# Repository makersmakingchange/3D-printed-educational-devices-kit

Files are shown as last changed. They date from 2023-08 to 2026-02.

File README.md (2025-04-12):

# 3D-Printed-Educational-Devices-Kit
<!--- 
SUMMARY
 --->

The [3D Printed Educational Devices Kit](https://www.makersmakingchange.com/s/product/3d-printed-educational-devices-kit/01tJR0000006949YAA) contains devices that support people with disabilities in activities of daily living and learning. These devices assist people with arthritis, limited finger exterity or other disabilities. This kit gives schools a great introduction into the world of 3D printed Assistive Technology (AT).

## 3D Printed Educational Devices Kit
### Summary

| Name                 | Repository Link |
|----------------------|-----------------|
| Bottle Opener        | https://makersmakingchange.com/s/product/bottle-opener/01tJR00000068z0YAA |  
| Key Turner           |  https://www.makersmakingchange.com/s/product/key-turner/01tJR00000068z6YAA  |
| Pen Ball             | https://www.makersmakingchange.com/s/product/pen-ball/01tJR00000068zzYAA |
| Palm Pen Holder      | https://www.makersmakingchange.com/s/product/palm-pen-holder/01tJR00000068z8YAA |
| Ready Bar Flat       | https://makersmakingchange.com/s/product/reading-bar-flat/01tJR00000068z3YAA |
| Dice Spinner         | https://makersmakingchange.com/s/product/dice-spinner/01tJR000000693qYAA |
| MMC60 Switch         | https://makersmakingchange.com/s/product/mmc60-switch/01tJR000000693rYAA |

### Bottle Opener
This device provides a large gripping surface and clamps onto the caps of standard water bottles with a small squeeze, allowing users to remove or screw on water bottle caps.

### Key Turner
Users loop their finger through the hole and twist to lock and unlock doors with minimal wrist movement. The large key bed can accommodate various shape of key heads.

### Pen Ball
The pen ball makes it easier to grip a pen, pencil, or other writing utensils.

### Palm Pen Holder
Users can gently curl their fingers around a handle to hold it securely or hook their thumb around the writing utensil

### Reading Bar Flat
The dyslexia bar is a tool that isolates text on a page so readers can focus on reading one or two lines at a time. This reading bar can be used on flat documents and sheets of paper.

### Dice Spinner
The switch activated dice spinner utilizes a hobby motor, battery holder, and jack along with a couple 3d printed parts and a clear plastic cup to make any dice game more accessible. It is an easy toy to make that allows children to roll the dice in an alternative way.

### MMC60 Switch
The switch is activated by applying pressure on the top surface. This switch can be connected to any standard AT interface, and can also be used with the Xbox Adaptive Controller. The kit contains different colours and textures of interchangeable button tops.

----

<!-- ABOUT MMC START -->
## About Makers Making Change
[Makers Making Change Logo](https://www.makersmakingchange.com/)

Makers Making Change is a program of [Neil Squire](https://www.neilsquire.ca/), a Canadian non-profit that uses technology, knowledge, and passion to empower people with disabilities.

Makers Making Change leverages the capacity of community based Makers, Disability Professionals and Volunteers to develop and deliver affordable Open Source Assistive Technologies.

 - Website: [www.MakersMakingChange.com](https://www.makersmakingchange.com/)
 - GitHub: [makersmakingchange](https://github.com/makersmakingchange)
 - Bluesky: [@makersmakingchange.bsky.social](https://bsky.app/profile/makersmakingchange.bsky.social)
 - Instagram: [@makersmakingchange](https://www.instagram.com/makersmakingchange)
 - Facebook: [makersmakechange](https://www.facebook.com/makersmakechange)
 - LinkedIn: [Neil Squire Society](https://www.linkedin.com/company/neil-squire-society/)
 - Thingiverse: [makersmakingchange](https://www.thingiverse.com/makersmakingchange/about)
 - Printables: [MakersMakingChange](https://www.printables.com/@MakersMakingChange)

### Contact Us
For technical questions, to get involved, or to share your experience we encourage you to [visit our website](https://www.makersmakingchange.com/) or [contact us](https://www.makersmakingchange.com/s/contact).
<!-- ABOUT MMC END -->

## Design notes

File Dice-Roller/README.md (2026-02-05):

# Rumble Plate Dice Roller
A switch adapted device to roll the dice for any game night!

This switch activated dice roller utilizes a hobby motor, battery holder, Omron switch, and 3.5mm jack along with a couple 3d printed parts and a clear plastic cup to make any dice game more accessible. This device is a new development of the Dice Spinner that features faster dice rolling and variations in allowable cup size.

The Rumble Plate Dice Roller allows for approximately 10oz to 22oz clear plastic cups. Following the assembly guide, the components can be wired and mounted, then the dice roller is all ready to use! It is an easy toy to make that allows people to roll the dice in an alternative way.

## Usage

An AT switch can be plugged into the 3.5mm jack on the side of the device to be used for activation. Alternatively, the on-device switch can be used for activation. The on-device button would be meant more for others playing around the table who are able to reach over and wrap their hands around the base to push the button. With the additional print of the vertical push base, the on-device button can be used to turn the device itself into the activation button such that anyone around the table can push on to top of  the clear cup to roll the dice. This on-device button can be used in tandem with the corded AT switch.

## Required Skills:

 - Soldering
 - 3D Printing

## Required Components

 - Motor
 - AAA Battery Holder
 - Velcro
 - Omron Switch
 - 3.5mm Jack
 - Clear Plastic Cup
 - Dice
 - 3D Printed Parts

## Printing Instructions

- Print the STL files in their given orientations
- 0.3 mm Layer height
- No supports
- No brim

## Build Instructions

This device consists of several 3D printed components and electrical components that assemble together and can be used in tandem with an assistive switch. All STL’s and documentation can be found in the downloadable maker files in the GitHub Repository.

<!-- ABOUT MMC START -->
## About Makers Making Change
[Makers Making Change Logo](https://www.makersmakingchange.com/)

Makers Making Change is a program of [Neil Squire](https://www.neilsquire.ca/), a Canadian non-profit that uses technology, knowledge, and passion to empower people with disabilities.

Makers Making Change leverages the capacity of community based Makers, Disability Professionals and Volunteers to develop and deliver affordable Open Source Assistive Technologies.

 - Website: [www.MakersMakingChange.com](https://www.makersmakingchange.com/)
 - GitHub: [makersmakingchange](https://github.com/makersmakingchange)
 - Bluesky: [@makersmakingchange.bsky.social](https://bsky.app/profile/makersmakingchange.bsky.social)
 - Instagram: [@makersmakingchange](https://www.instagram.com/makersmakingchange)
 - Facebook: [makersmakechange](https://www.facebook.com/makersmakechange)
 - LinkedIn: [Neil Squire Society](https://www.linkedin.com/company/neil-squire-society/)
 - Thingiverse: [makersmakingchange](https://www.thingiverse.com/makersmakingchange/about)
 - Printables: [MakersMakingChange](https://www.printables.com/@MakersMakingChange)

### Contact Us
For technical questions, to get involved, or to share your experience we encourage you to [visit our website](https://www.makersmakingchange.com/) or [contact us](https://www.makersmakingchange.com/s/contact).
<!-- ABOUT MMC END -->

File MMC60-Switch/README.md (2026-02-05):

<!-- Open Source Assistive Technology: GitHub Readme Template Version 1.1 (2024-Mar-15) -->

<!---
INSTRUCTIONS
This is a markdown template for creating the README.md file in a GitHub repository. This file is rendered and displayed automatically when someone visits the repository.

This document includes helper text that will not be displayed when rendered. Any text between the less-than sign + exclamation mark + three hyphen-minus (<!---) and matching three hyphen-minus + greater-than sign will not be displayed. This helper text can be deleted once the corresponding section is completed.

This template has a number of fields that can be searched and replaced with other text:
 - <Device_Name> Replace this with filename-friendly version of the device with underscores. e.g., Open_Wobble_Switch
 - <DeviceName> Replace this with the human-readable name of the device with spaces. e.g., Open Wobble Switch
 - <DesignerName> Replace this with the person or organization responsible for the design. e.g., John Doe.
 - <RepositoryLink> Replace this with the web address for the repository. e.g., (e.g., https://github.com/makersmakingchange/Open-Wobble-Switch))
 - <MMCWebLink> This is an alphanumeric id for the Makers Making Change Website. e.g., 01tJR000000698oYAA. This will come from MMC staff. 
 --->
 
 <!--- 
TITLE
Should match the name of the GitHub repository. Choose something descriptive rather than whimsical. 
 --->
# MMC60 Assistive Switch

2025-May-02: This repository is in the process of updating.

<!--- SUMMARY A brief summary of the project. What it does, who it is for, how much it costs.  --->
The <DeviceName> is an assistive technology widget that makes it easier to document Open-Source Assistive Technology devices. 

It is intended for use by makers. 

The device is comprised of off-the-shelf electronics and 3D printed parts. 

The overall cost of materials is about $<MaterialCost> (plus $<ShippingCost> for component shipping).

Picture of <DeviceName>.

## More info at
- [Makers Making Change Assistive Device Library Listing](<MMCWebLink>)

## How to Obtain the Device
### 1. Do-it-Yourself (DIY) or Do-it-Together (DIT)

This is an open-source assistive technology, so anyone is free to build it. All of the files and instructions required to build the device are contained within this repository. Refer to the Maker Guide below.

### 2. Request a build of this device

You may also submit a build request through the [Makers Making Change Assistive Device Library Listing](<MMCWebLink>) to have a volunteer maker build the device. As the requestor, you are responsible for reimbursing the maker for the cost of materials and any shipping.

### 3. Build this device for someone else

If you have the skills and equipment to build this device, and would like to donate your time to create the device for someone who needs it, visit the [MMC Maker Wanted](https://makersmakingchange.com/maker-wanted/) section.

## Build Instructions

### 1. Read through the Maker Guide

The [Maker Guide](/Documentation/<Device_Name>_Maker_Guide.pdf)  contains all the necessary information to build this device, including tool lists, assembly instructions, programming instructions (if applicable) and testing.

### 2. Order the Off-The-Shelf Components

The [Bill of Materials](/Documentation/<Device_Name>_BOM.xlsx) lists all of the parts and components required to build the device.

### 3. Print the 3D Printable components

All of the files and individual print files can be in the [/Build_Files/3D_Printing_Files](/Build_Files/3D_Printing_Files/) folder.

### 4. Assemble the <DeviceName>

Reference the [Assembly Guide](/Documentation/<Device_Name>_Assembly_Guide.pdf) for the tools and steps required to build each portion.

## How to improve this Device
As open source assistive technology, you are welcomed and encouraged to improve upon the design. 

## Files
### Documentation
| Document             | Version | Link |
|----------------------|---------|------|
| Design Rationale     | 1.0     | [<DeviceName>_Design_Rationale](/Documentation/<Device_Name>_Design_Rationale.pdf)     |
| Maker Guide          | 1.0     | [<DeviceName>_Maker_Checklist](/Documentation/<Device_Name>_Maker_Guide.pdf)     |
| Bill of Materials    | 1.0     | [<DeviceName>_Bill_of_Materials](/Documentation/<Device_Name>_BOM.xlsx)     |
| User Guide           | 1.0     | [<DeviceName>_User_Guide](/Documentation/<Device_Name>_Quick_Guide.pdf)    |
| Changelog            | 1.0     | [Changelog](CHANGES.txt)     |

### Design Files
<!---
DESIGN FILES
Include a copy of the original design files to facilitate easy editing and customization. Consider also including a generic format (e.g., STEP)
--->
 - [CAD Files](/Design_Files/CAD_Design_Files)
 - [PCB Files](/Design_Files/PCB_Design_Files)

<!---
BUILD FILES
Include a copy of the build files intended for manufacturing. This may include svg files for laser cutting, stl files for 3d printing, Gerber files for custom PCBs, and Arduino files for custom firmware
--->
### Build Files
 - [3D Printing Files](/Build_Files/3D_Printing_Files)
 - [PCB Build Files](/Build_Files/PCB_Build_Files)
 - [Firmware Files](/Build/Firmware_Files)

<!---
ATTRIBUTION
Provide any necessary attribution for designs or components that are included in the device or as part of the project.
--->
## Attribution

The device was designed by <DesignerName>. 

<!---
This is the attribution for the template.
--->
The documentation template was created by Makers Making Change / Neil Squire Society and is used under a CC BY-SA 4.0 license. It is available at the following link: [https://github.com/makersmakingchange/OpenAT-Template](https://github.com/makersmakingchange/OpenAT-Template)

<!---
CONTRIBUTORS
List the names of the people that contributed to the design. This could include the original source of the idea, designers, testers, documenters, etc.
--->
### Contributors

Designers:
 - Designer 1 
 - Designer 2

<!---
LICENSE
Add the year(s) for the copyright and the Designer Name. You may use the standard set of open licenses or choose your own for the hardware, software, and accompanying materials.
--->
## License
Copyright (c) YYYY <DesignerName>.

This repository describes Open Hardware:
 - Everything needed or used to design, make, test, or prepare the <Device-Name> is licensed under the [CERN 2.0 Weakly Reciprocal license (CERN-OHL-W v2) or later](https://cern.ch/cern-ohl ) .
 - All software is under the [GNU General Public License v3.0 (GPL-3.0)](https://www.gnu.org/licenses/gpl.html).
 - Accompanying material such as instruction manuals, videos, and other copyrightable works that are useful but not necessary to design, make, test, or prepare the <Device-Name> are published under a [Creative Commons Attribution-ShareAlike 4.0 license (CC BY-SA 4.0)](https://creativecommons.org/licenses/by-sa/4.0/) .

You may redistribute and modify this documentation and make products using it under the terms of the [CERN-OHL-W v2](https://cern.ch/cern-ohl).
This documentation is distributed WITHOUT ANY EXPRESS OR IMPLIED WARRANTY, INCLUDING OF MERCHANTABILITY, SATISFACTORY QUALITY AND FITNESS FOR A PARTICULAR PURPOSE.
Please see the CERN-OHL-W v2 for applicable conditions.

Source Location: <Repository_Link> 

---

<!-- ABOUT MMC START -->
## About Makers Making Change
[Makers Making Change Logo](https://www.makersmakingchange.com/)

Makers Making Change is a program of [Neil Squire](https://www.neilsquire.ca/), a Canadian non-profit that uses technology, knowledge, and passion to empower people with disabilities.

Makers Making Change leverages the capacity of community based Makers, Disability Professionals and Volunteers to develop and deliver affordable Open Source Assistive Technologies.

 - Website: [www.MakersMakingChange.com](https://www.makersmakingchange.com/)
 - GitHub: [makersmakingchange](https://github.com/makersmakingchange)
 - Bluesky: [@makersmakingchange.bsky.social](https://bsky.app/profile/makersmakingchange.bsky.social)
 - Instagram: [@makersmakingchange](https://www.instagram.com/makersmakingchange)
 - Facebook: [makersmakechange](https://www.facebook.com/makersmakechange)
 - LinkedIn: [Neil Squire Society](https://www.linkedin.com/company/neil-squire-society/)
 - Thingiverse: [makersmakingchange](https://www.thingiverse.com/makersmakingchange/about)
 - Printables: [MakersMakingChange](https://www.printables.com/@MakersMakingChange)

### Contact Us
For technical questions, to get involved, or to share your experience we encourage you to [visit our website](https://www.makersmakingchange.com/) or [contact us](https://www.makersmakingchange.com/s/contact).
<!-- ABOUT MMC END -->

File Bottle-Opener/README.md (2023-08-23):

# Bottle-Opener
The Bottle Opener is a simple, low-cost, 3D-printable handheld tool to help those with arthritis, limited finger dexterity or other related disabilities open or close plastic screw-on caps on various beverage bottles, cleaning products, condiments. The bottle opener allows users to remove or replace the lids of these jugs with a small squeeze on a large, rounded gripping surface. The Bottle Opener has several modified versions to open different sizes of containers. The different sizes are named by the approximate diameter of the caps they can open in millimeters.

Bottle_Opener

## More info at
- [Makers Making Change Project Page](https://makersmakingchange.com/project/bottle-opener/)
- [Makers Making Change Forum Thread](https://makersmakingchange.com/forum/topic/bottle-opener-for-arthritis)

## Getting Started

### 1. Print the 3D Printable components

Print the components according to the instructions in the [3D Print Guide](/Documentation/Bottle_Opener_3D_Print_Guide_V1.0.pdf).

All of the files and individual print files can be in the [/Build_Files](/Build_Files) folder.

### 2. Sizing

There are 5 different sizes of bottle opener to suit the different sizes of plastic caps on various bottles and containers. The [Summary](/Documentation/Bottle_Opener_Summary_V1.0.pdf) contains information on examples of different bottles that can be opened with the different sizes of bottle openers. A [Printable Sizing Sheet](/Documentation/Bottle_Opener_Printable_Sizing_Chart.pdf) has been provided to match bottle caps to the suitable bottle opener. Make sure to check "actual size" in the print settings so the image remains to-scale.

### 3. Bill of Materials

The [Bill of Materials](/Documentation/Bottle_Opener_BOM_V1.0.csv) lists the cost of building the different sizes of Bottle Openers.

## Files
### Documentation
| Document              | Version | Link |
|-----------------------|---------|------|
| Summary               | 1.0     | [Bottle_Opener_Summary](/Documentation/Bottle_Opener_Summary_V1.0.pdf)     |
| 3D Print Guide        | 1.0     | [Bottle_Opener_3D_Print_Guide](/Documentation/Bottle_Opener_3D_Print_Guide_V1.0.pdf)     |
| Design Rationale      | 1.0     | [Bottle_Opener_Design_Rationale](/Documentation/Bottle_Opener_Design_Rationale_V1.0.pdf)     |
| Bill of Materials     | 1.0     | [Bottle_Opener_Bill_of_Materials](/Documentation/Bottle_Opener_BOM_V1.0.csv)     |
| Maker Checklist       | 1.0     | [Bottle_Opener_Maker_Checklist](/Documentation/Bottle_Opener_Maker_Checklist_V1.0.pdf)     |
| User Guide            | 1.0     | [Bottle_Opener_User_Guide](/Documentation/Bottle_Opener_User_Guide_V1.0.pdf)    |
| Changelog             | 1.0     | [Bottle_Opener_Changelog](/Documentation/Bottle_Opener_Changelog_V1.0.pdf)     |
| Printable Sizing Chart| 1.0     | [Bottle_Opener_Printable_Sizing_Chart](/Documentation/Bottle_Opener_Printable_Sizing_Chart.pdf)     |

### Design Files
[CAD Files](/Design_Files)

### Build Files
 - [3D Printing Files](/Build_Files)

## Attribution
Designers:
 - Neil Squire / Makers Making Change

## License
<br /><span xmlns:dct="http://purl.org/dc/terms/" property="dct:title">Bottle Opener</span> by <a xmlns:cc="http://creativecommons.org/ns#" href="www.makersmakingchange.com" property="cc:attributionName" rel="cc:attributionURL">Neil Squire</a> is licensed under a <a rel="license" href="http://creativecommons.org/licenses/by-sa/4.0/">Creative Commons Attribution-ShareAlike 4.0 International License</a>.

## About Us
Makers Making Change Logo

Makers Making Change is an initiative of [Neil Squire](https://www.neilsquire.ca/), a Canadian non-profit that helps people with disabilities.

We are committed to creating a network of volunteer makers who support people with disabilities in their communities through 3D printing assistive devices. Check out our library of free, open-source assistive technologies with parts and build instructions.

 - [www.MakersMakingChange.com](https://www.makersmakingchange.com/)
 - [GitHub](https://github.com/makersmakingchange)
 - [Thingiverse](https://www.thingiverse.com/makersmakingchange/about)
 - Twitter: [@makermakechange](https://twitter.com/makermakechange)
 - Instagram: [@makersmakingchange](https://www.instagram.com/makersmakingchange)

## Contact Us

For technical questions, to get involved, or share your experience we encourage you to visit the [MMC Project Page]( https://www.makersmakingchange.com/project), [MMC Forum](https://forum.makersmakingchange.com), or contact info@makersmakingchange.com

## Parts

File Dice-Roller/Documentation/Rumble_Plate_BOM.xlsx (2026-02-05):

Device: Rumble Plate Dice Tumbler |  |  |  |  |  | Total Cost | Total Print time (hr) | Total filament (g)
Version: V2.0 | Date Created: 9/14/2021 |  |  |  |  | $13.60 | 4.12 | 82.65
Commercial Parts:
Part type (Electrical. Mechanical, Sanitization, ect) | Part | Quantity Needed | Pkg Quantity | Price per package | Price per Unit | Price for qty needed |  | Link
Electrical | DC Motor | 1 | 1 | $2.66 | $2.66 | $2.66 |  | https://www.digikey.ca/en/products/detail/adafruit-industries-llc/711/5353610
Electrical | 3.5mm Mono Jack | 1 | 1 | $2.17 | $2.17 | $2.17 |  | https://www.digikey.ca/short/pq1d1z
Electrical | Switch (Omron B50503F-) | 1 | 1 | $0.94 | $0.94 | $0.94 |  | https://www.digikey.ca/short/jvzq2d
Electrical | Battery Holder | 1 | 1 | $1.69 | $1.69 | $1.69 |  | 2271 Kitronik Ltd. | Battery Products | DigiKey (https://www.digikey.ca/en/products/detail/kitronik-ltd/2271/8635436?productid=8635436)
Mechanical | Cup | 1 | 50 | $4.47 | $0.09 | $0.09 |  | https://www.walmart.ca/en/ip/great-value-plastic-party-cups-clear/6000198044907
Mechanical | Dice | 2 | 5 | $5.00 | $1.00 | $2.00 |  | https://www.walmart.ca/en/ip/ACE-Dice-5ct/PRD54IXGNXVYTJP
Electrical | AAA Batteries | 2 | 2 | $1.98 | $0.99 | $1.98 |  | https://www.walmart.ca/en/ip/energizer-max-alkaline-aaa-batteries-2-pack/PRD3IIHXYVK66QB
3D Printed Parts ESTIMATED PRICING USING 1KG ROLL COST: | $25.00
Part (estimated with 0.3 mm layer height) | Description | Quantity Needed | TOTAL Mass (g) | Estimated Price | Print Time (Min) | Link
Base | 3D printed Part | 1 | 42.85 | $1.07 | 124
Cam | 3D printed Part | 1 | 0.76 | $0.02 | 5
Retaining Ring | 3D printed Part | 1 | 7.86 | $0.20 | 22
Button | 3D printed Part | 1 | 1.03 | $0.03 | 5
Plate | 3D printed Part | 1 | 15.16 | $0.38 | 40
Lid | 3D printed Part | 1 | 14.99 | $0.37 | 51
 |  |  | Total Print Cost: | $2.07
Tools for Assembly
soldering iron
Pliers
Wire Cutters
Wire Strippers
Sharp Knife
Alternatives (if there are other sources for some parts link them below)
Part and description | Link
Cups | Free from a coffee shop/restaurant
DC Motor | Brushed DC Motor 2 (RM2) - RobotShop (https://www.robotshop.com/ca/en/solarbotics-regular-motor-2.html)
DC Motor (Bulk) | https://www.amazon.ca/Gikfun-Motor-Electric-Arduino-EK1291x10C/dp/B06WLL6QM5?hvadid=292968375828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

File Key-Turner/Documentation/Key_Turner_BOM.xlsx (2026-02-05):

Device: | Key Turner
Version: | V1.0
Last Updated: | 2026-02-04
 |  |  |  |  |  |  |  | Total filament (g) |  | Unit Cost | Total Estimated Cost | Build Cost
 |  |  |  |  |  |  |  | 12.44 |  | $1.69 | $8.45
ID | Commercial Parts |  |  |  |  |  |  |  |  | $1.38 | $8.14
 | Part | Description |  | Manufacturer | Supplier | QTY / Device | QTY / PKG | PKGs | $/ PKG | $ / Device | Total Estimated Cost |  | Link
 |  | M4 x 12 mm bolt |  |  |  | 1 | 5 | 1 | $3.99 | $0.80 | $3.99 |  | https://www.homehardware.ca/en/5-pack-m4-x-12mm-zinc-plated-pan-head-machine-screws/p/2122013
 |  | M4 hex nut |  |  |  | 1 | 1 | 1 | $0.18 | $0.18 | $0.18 |  | https://www.homedepot.ca/product/paulin-m4-0-70-class-8-metric-hex-nut-din-934-zinc-plated/1000128515
 |  | M4 Washer |  |  |  | 2 | 20 | 1 | $3.97 | $0.40 | $3.97 |  | https://www.homedepot.ca/product/paulin-metric-flat-washers-4mm-20pcs/1001588032
 | 3D Printed Parts |  |  |  |  |  |  | 12.44 |  | $0.31 | $0.31
 | Part | Description | Filament Type | Filament | Color | QTY / Device | Mass (g) / Part | Total Mass | $ / kg | $ / Device | Total Estimated Cost |  | Link
 | Key_Turner.stl | Key turner body | PLA |  | Any | 1 | 12.44 | 12.44 | $25.00 | $0.31 | $0.31
 | Tools | *Tools are only required when attaching the key to the key turner*
 | Tool | Description |  | Manufacturer | Supplier |  |  |  |  |  |  |  | Link
 | Screw driver | Screwdriver that matches the head of the bolts purchased
 | Wrench/pliers | To hold the nut while tightening the bolt
 | Alternatives
 | Part | Description |  | Manufacturer | Supplier | QTY / Device | QTY / PKG | PKGs | $/ PKG | $ / Device | Total Estimated Cost |  | Link
 |  | #8-1/2" bolt |  |  |  | 1
 |  | #8 hex nut |  |  |  | 1
 |  | #8 washers |  |  |  | 2

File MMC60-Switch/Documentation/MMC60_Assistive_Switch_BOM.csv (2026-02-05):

Device: MMC60_Assistive_Switch |  | Total Cost | Total Print time (hr) | Total filament (g)
Version: V1.0 | Date Created: Feb 2, 2026 | $12.14 | 1.97 | 39.4
Commercial Parts:
Part type (Electrical. Mechanical, Sanitization, ect) | Part Name | Quantity Needed | Pkg Quantity | Price per package | Price per Unit | Price for qty needed | Link
 | 3.5mm Mono Jack | 1 | 1 | $2.47 | $2.47 | $2.47 | https://www.digikey.ca/en/products/detail/cui-inc/MJ-3502/281321
 | #4 3/8 length screw | 5 | 1 | $0.52 | $0.52 | $2.59 | https://www.digikey.ca/en/products/detail/serpac/6005/307599
 | 1/4-20 Hex nut | 2 | 1 | $0.22 | $0.22 | $0.44 | https://www.digikey.ca/en/products/detail/80-20-llc/24202/28311218
 | 1/4-20, 1/2" length Hex Bolt | 1 | 1 | $0.58 | $0.58 | $0.58 | https://www.homedepot.ca/product/paulin-1-4-20-x-1-2-inch-hex-head-cap-screw-18-8-stainless-steel-unc/1000142251
 | 1/4-20, 5/16" length T-Nut | 1 | 1 | $0.55 | $0.55 | $0.55 | https://www.homedepot.ca/product/paulin-1-4-inch-20-tee-nuts-4-prong-5-16-inch-barrel-length/1000129429
 | 3.5 mm Mono Cable, 10 ft, Male to Male | 1 | 1 | 2.89 | $2.89 | $2.89 | https://www.primecables.ca/p-370665-cab-aud-200-all-35mm-18-inch-mono-ts-male-to-male-28awg-ft4-cable-black
 | Limit Switch | 1 | 1 | 1.55 | $1.55 | $1.55 | https://www.digikey.ca/en/products/detail/omron-electronics-inc-emc-div/SS-3GP/664724
3D Printed Parts ESTIMATED PRICING USING 1KG ROLL COST: | $25.00
Part | Description | Quantity Needed | TOTAL Mass (g) | Estimated Price | Print Time (Min) | Link
MMC60_Base_Bottom_EN-FR |  | 1 | 20.74 | $0.52 | 56
MMC60_Button |  | 1 | 9.2 | $0.23 | 24
RFS_Base_Top |  | 1 | 5.67 | $0.14 | 16
RFS_Flexure |  | 1 | 3.53 | $0.09 | 15
RFS_Pins |  | 1 | 0.26 | $0.01 | 7
RFS_Sw_Jack_Mount |  | 1 | 3.54 | $0.09 | 15
 |  |  | Total Print Cost: | $1.07
Tools for Assembly
Alternatives (if there are other sources for some parts link them below)
Part and description | Link
#4 3/8 length screw | https://a.co/d/0fvi6Sdn
1/4-20 Hex nut | https://a.co/d/04irVJAz
1/4-20, 1/2" length Hex Bolt | https://a.co/d/0aEeQ1J0
1/4-20, 5/16" length T-Nut | https://a.co/d/083bJTZo

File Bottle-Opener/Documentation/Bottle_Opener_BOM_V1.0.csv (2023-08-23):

Device: Bottle_Opener |  | Total Cost | Total Print time (hr) | Total filament (g)
Version: V1.0 | Date Created: 5/18/2022 | $4.65 | 3.78 | 37
3D Printed Parts ESTIMATED PRICING USING 1KG ROLL COST: | $25.00
Part | Description | Quantity Needed | TOTAL Mass (g) | Estimated Price | Print Time (Min) | Link
Bottle_Opener_30.stl | STL file for full functional bottle opener with nominal diameter of approx. 30 mm. | 1 | 37 | $0.93 | 227 | Bottle-Opener/Build_Files at main · makersmakingchange/Bottle-Opener (github.com)
Bottle_Opener_35.stl | STL file for full functional bottle opener with nominal diameter of approx. 30 mm. | 1 | 36 | $0.90 | 224
Bottle_Opener_40.stl | STL file for full functional bottle opener with nominal diameter of approx. 30 mm. | 1 | 36 | $0.90 | 226
Bottle_Opener_45.stl | STL file for full functional bottle opener with nominal diameter of approx. 30 mm. | 1 | 38 | $0.95 | 231
Bottle_Opener_50.stl | STL file for full functional bottle opener with nominal diameter of approx. 30 mm. | 1 | 39 | $0.98 | 241
 |  |  | Total Print Cost: | $4.65

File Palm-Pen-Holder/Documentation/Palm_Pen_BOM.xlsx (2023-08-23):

Device: Palm Pen Holder |  | Total Cost | Total Print time (hr) | Total filament (g)
Version: V1.0 | Date Created: 06/30/2023 | $1.72 | 8.33 | 50
Commercial Parts:
Part type (Electrical. Mechanical, Sanitization, ect) | Part Name | Quantity Needed | Pkg Quantity | Price per package | Price per Unit | Price for qty needed | Link
Hardware | M4- 0.70 Machine Screw Nut | 1 | 16 | $2.97 | $0.19 | $0.19 | https://www.homedepot.ca/product/paulin-metric-hex-nut-m4-70-16pcs/1001588036
Hardware | M4- 0.70 X 16 Machine Screw | 1 | 12 | $3.47 | $0.29 | $0.29 | https://www.homedepot.ca/product/paulin-pan-square-machine-screw-m4-70-x-16-12pcs/1001588009
3D Printed Parts ESTIMATED PRICING USING 1KG ROLL COST: | $25.00
Part | Description | Quantity Needed | TOTAL Mass (g) | Estimated Price | Print Time (Min) | Link
x_Palm_Pen_y_Pen_hole.STL Where “x” is the Palm Pen Holder device sizing and “y” is the pen hole sizing | File including the single piece Palm Pen Holder device | 1 | 50 | $1.25 | 500
 |  |  | Total Print Cost: | $1.25
Tools for Assembly
3D Printer
Screw Driver
Alternatives (if there are other sources for some parts link them below)
Part and description | Link
Note that some printers are less accurate and M4 size hardware may not fit. It is recommended that you go to a hardware store and test different bolt sizes for the palm pen that is created

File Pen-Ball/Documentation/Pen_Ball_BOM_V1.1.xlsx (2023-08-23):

Pen Ball |  | Total Cost | Total Print time (hr) | Total filament (g)
Version: V1.1 | Last Updated: 2023-Jun-30 | $3.07 | 8.33 | 47
Commercial Parts:
Part type (Electrical. Mechanical, Sanitization, ect) | Part Name | Quantity Needed | Pkg Quantity | Price per package | Price per Unit | Price for qty needed | Link
Hardware | M4- 0.70 Machine Screw Nut | 4 | 16 | $2.97 | $0.19 | $0.74 | https://www.homedepot.ca/product/paulin-metric-hex-nut-m4-70-16pcs/1001588036
Hardware | M4- 0.70 X 16 Machine Screw | 4 | 12 | $3.47 | $0.29 | $1.16 | https://www.homedepot.ca/product/paulin-pan-square-machine-screw-m4-70-x-16-12pcs/1001588009
3D Printed Parts ESTIMATED PRICING USING 1KG ROLL COST: | $25.00
Part | Description | Quantity Needed | TOTAL Mass (g) | Estimated Price | Print Time (Min) | Link
x_Pen_ball_y_Pen_hole.STL Where “x” is the pen ball sizing and “y” is the pen hole sizing | Pen ball STL includes both top and bottom of pen ball | 1 | 47 | $1.18 | 500
 |  |  | Total Print Cost: | $1.18
Tools for Assembly
3D Printer
Screw Driver
Alternatives (if there are other sources for some parts link them below)
Part and description | Link
Note that some printers are less accurate and M4 size hardware may not fit. It is recommended that you go to a hardware store and test different bolt sizes for the palm pen that is created

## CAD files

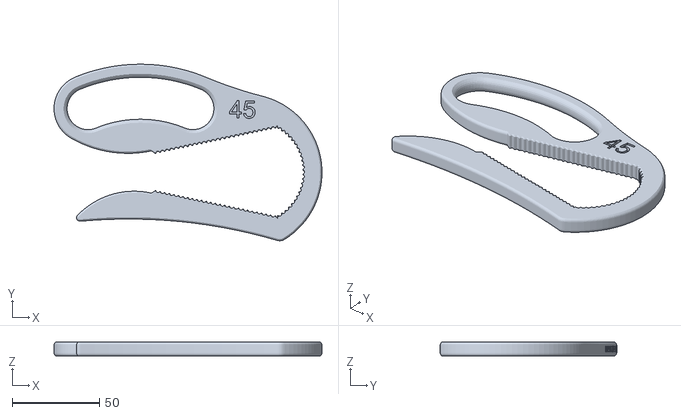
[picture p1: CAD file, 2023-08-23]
Bottle-Opener/Build_Files/Bottle_Opener_45.stl
153.5 x 101.2 x 8.00

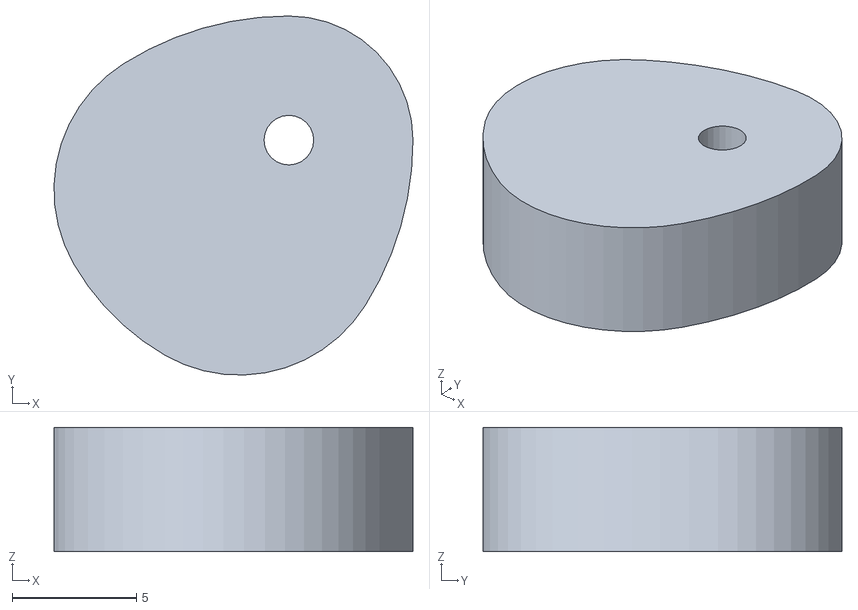
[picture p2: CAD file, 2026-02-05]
Dice-Roller/Build_Files/3D_Print_Files/Rumble_Plate_STLs/Rumble_Plate_Cam.stl
14.5 x 14.5 x 5.00

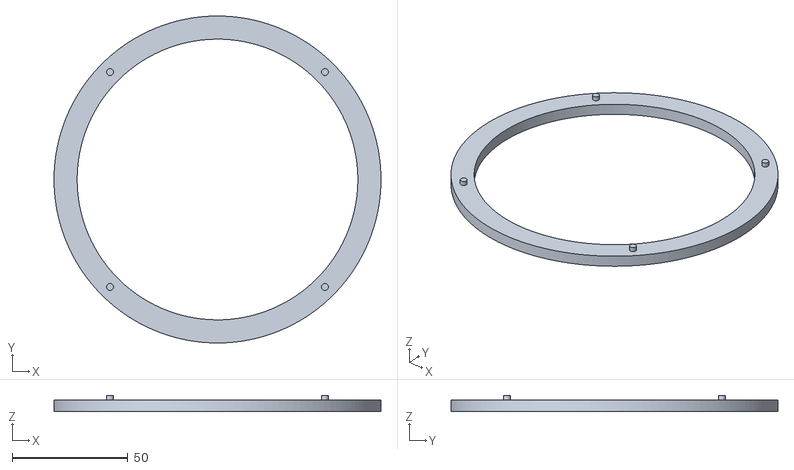
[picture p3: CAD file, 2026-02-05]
Dice-Roller/Build_Files/3D_Print_Files/Vertical_Push_Base_STLs/Vertical_Push_Base_bottom.stl
141.2 x 141.2 x 7.00

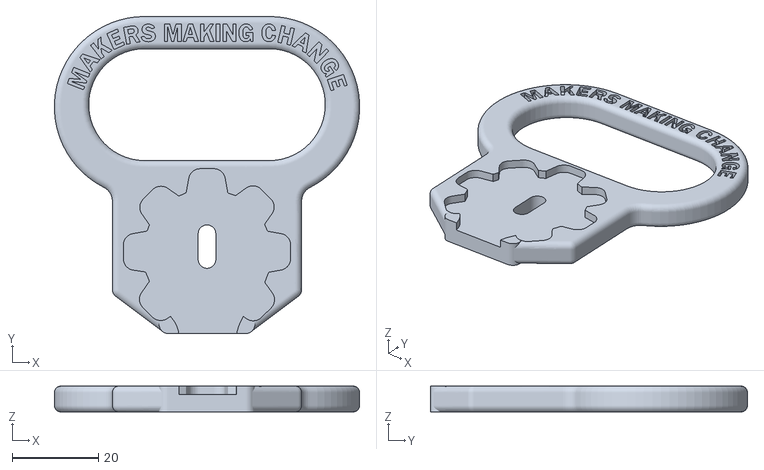
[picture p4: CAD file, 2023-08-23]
Key-Turner/Build_Files/3D_Print_Files/Key_Turner.stl
71.0 x 73.7 x 6.00

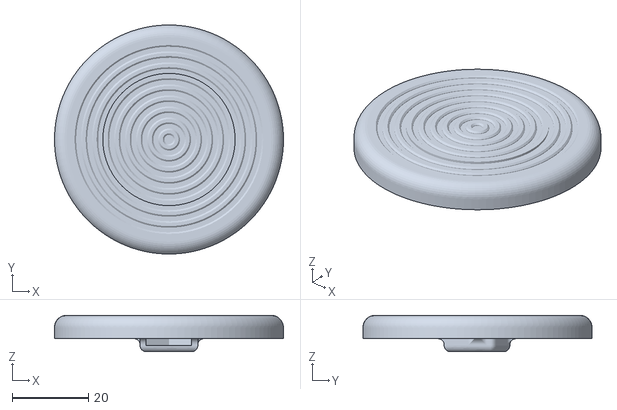
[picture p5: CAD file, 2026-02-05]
MMC60-Switch/Build_Files/3D_Printing_Files/Custom_Tops/MMC60_Button_Rings2.stl
60.0 x 60.0 x 9.56

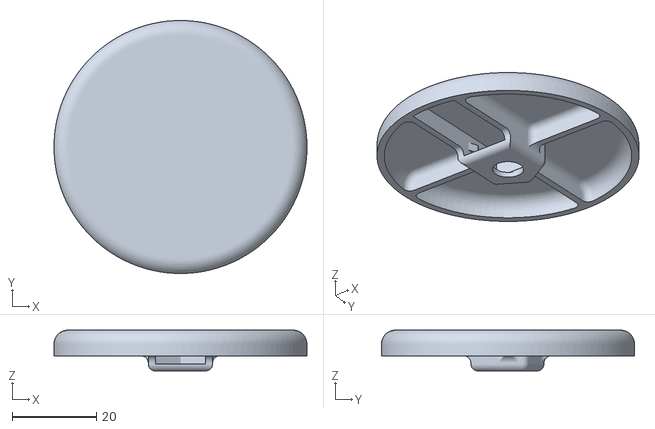
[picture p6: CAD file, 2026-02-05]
MMC60-Switch/Build_Files/3D_Printing_Files/MMC60_Button.stl
60.0 x 60.0 x 9.70

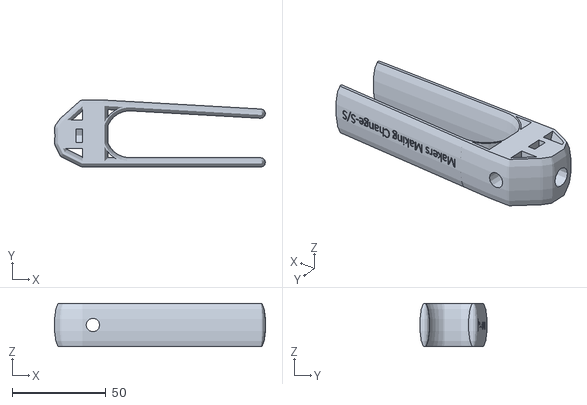
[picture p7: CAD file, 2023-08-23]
Palm-Pen-Holder/Build_Files/3D_Print_ Files/Small_Palm_Pen_Small_Pen_hole.stl
112.7 x 35.8 x 23.0

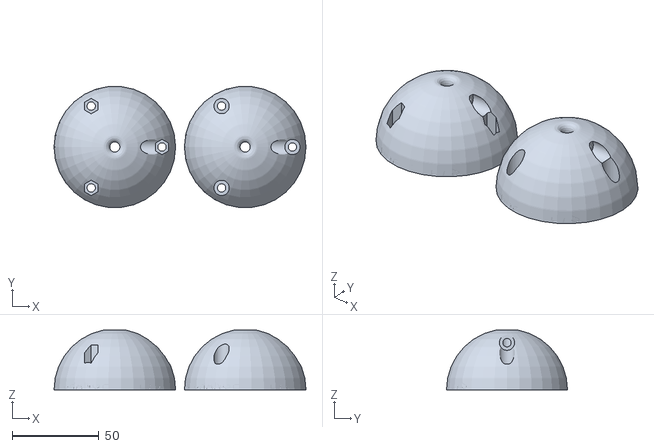
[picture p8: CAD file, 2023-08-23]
Pen-Ball/Build_Files/3D_Print_Files/Large_Pen_ball_Small_Pen_hole.stl
144.9 x 69.6 x 34.4

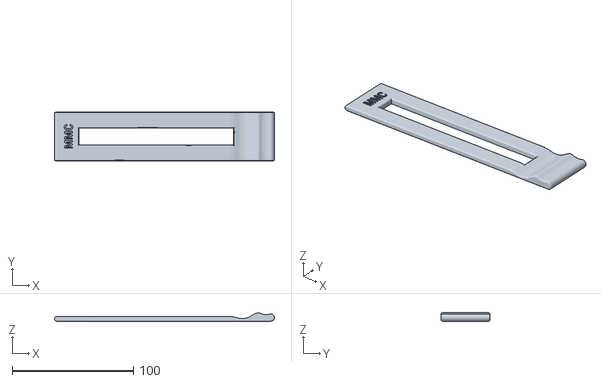
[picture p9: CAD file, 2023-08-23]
Reading-Bar-Flat/Build_Files/3D_Print_Files/Reading_Bar_Flat_Large_Window.STL
181.1 x 40.0 x 7.03

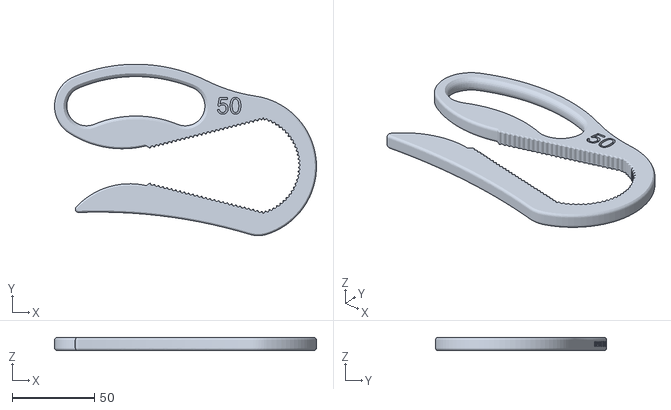
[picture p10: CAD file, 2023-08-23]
Bottle-Opener/Build_Files/Bottle_Opener_50.stl
159.5 x 104.4 x 8.00

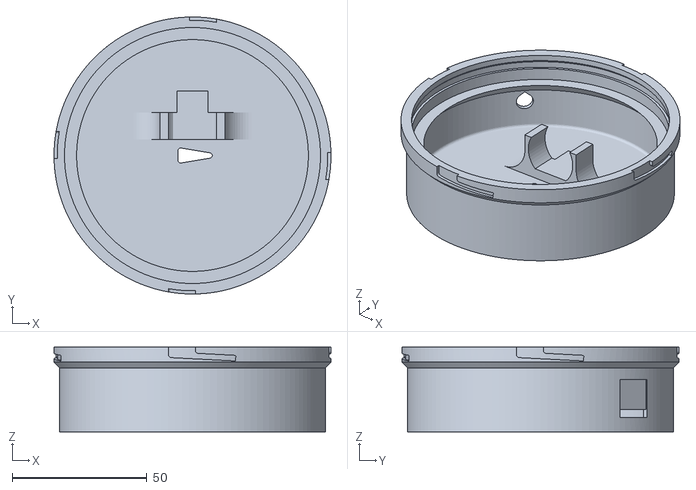
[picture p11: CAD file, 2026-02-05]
Dice-Roller/Build_Files/3D_Print_Files/Rumble_Plate_STLs/Rumble_Plate_Base.stl
102.9 x 102.9 x 31.5

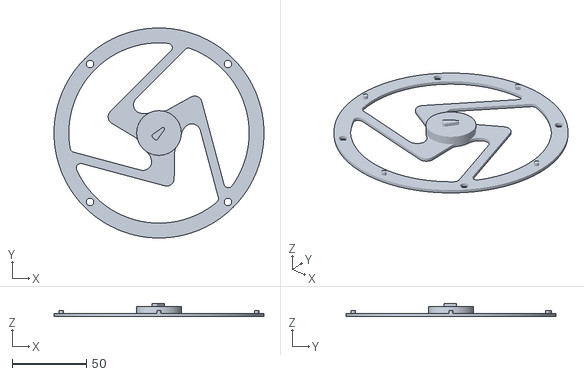
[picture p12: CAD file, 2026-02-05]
Dice-Roller/Build_Files/3D_Print_Files/Vertical_Push_Base_STLs/Vertical_Push_Base_flexure.stl
141.2 x 141.2 x 9.00

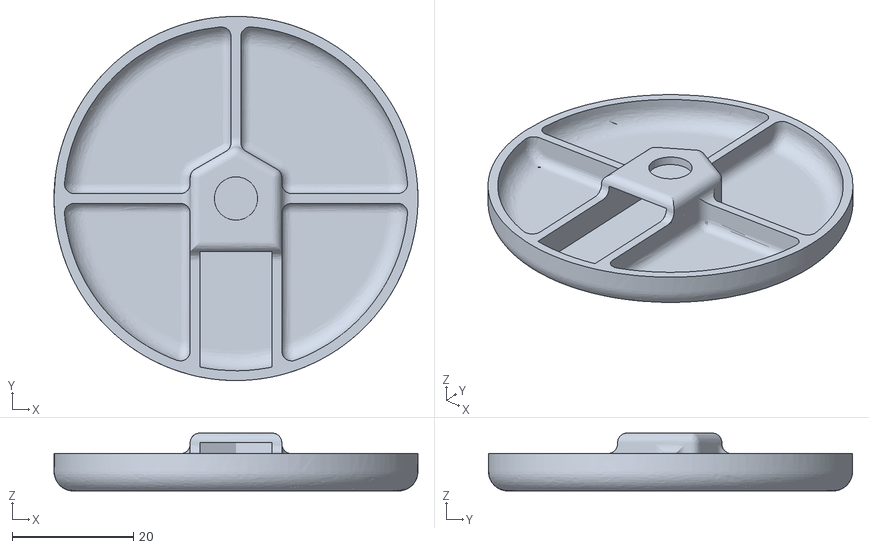
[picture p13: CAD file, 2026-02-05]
MMC60-Switch/Build_Files/3D_Printing_Files/Custom_Tops/RFS_B_Button.stl
60.0 x 60.0 x 9.55

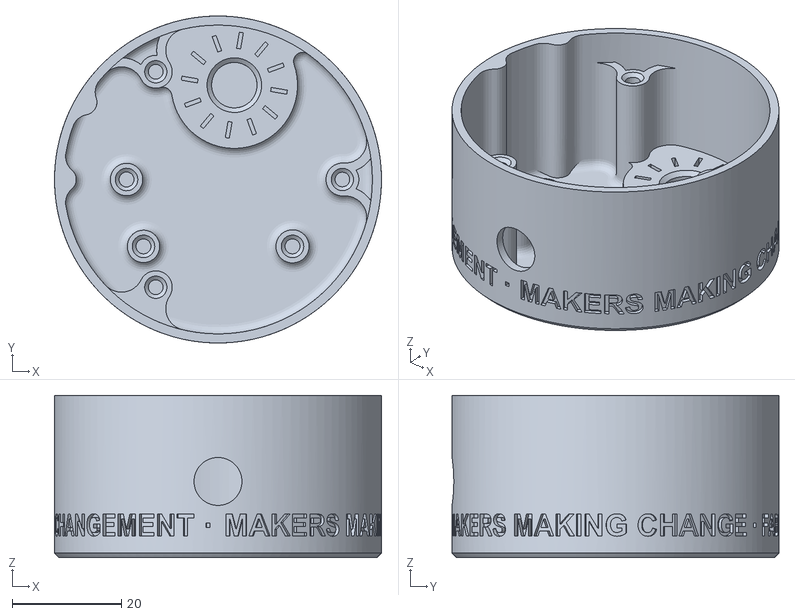
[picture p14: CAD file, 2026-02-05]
MMC60-Switch/Build_Files/3D_Printing_Files/MMC60_Base_Bottom_EN-FR.stl
60.0 x 60.0 x 29.8

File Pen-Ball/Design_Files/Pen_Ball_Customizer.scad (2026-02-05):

// parametric pen ball - scruss 2018-03
// CC BY-SA - Stewart Russell - scruss.com
// for Makers Making Change - http://makersmakingchange.com/

// you will need:
// * 5 off M4 x 12 stainless pan head machine screws
// * 5 off M4 stainless nuts

// ** the two main parameters **
// may produce a useless design, so change at your own risk
ball_diam = 60.0;   // 60 mm is default; can go to 45 if wall_thick reduced
pen_diam = 10.5;    // should fit most pens; 10.5 mm is default

// ** lesser parameters
wall_thick = 2.0;   // shell thickness; default 2, reduce to 1 for 45 mm diameter
tol=0.8;            // tolerance for loose fit
// *** NB: please do not explicitly set $fn ***
// and everything below here: HERE BE (smallish) DRAGONS

/* M4 nut and screw dimensions - sized for M4 x 12

Nut: 7 mm across flats, 3.2 mm thick
so across points = 7 / ((√3) / 2) ~= 8.1 mm
source: http://www.fairburyfastener.com/xdims_metric_nuts.htm

Screw:          4.0 mm, 4.7 to outside of thread
Length:        12 or 20 mm
Head height:    3.1 mm
Head diameter:  8.0 mm
source: https://spaenaur.com/pdf/sectionR/R11.pdf
*/
nut_thick =          3.2;
nut_flats =          7.0;
nut_diam =          nut_flats / (sqrt(3)/2);
screw_length =      12.0;            // M4 x 12
screw_nom_diam =     4.0;
screw_head_diam =    8.0;
screw_head_thick =  nut_thick;   // for simplicity
pillar_height =     screw_length - (1.25 * nut_thick);

/* bolt passages:
   since we're on a sphere, the height at
   radius x is given by
   
   y = 2 × √(r² - x²)
   
   this drops off very quickly as x → r
   so we probably won't need this
*/
function height_at_radius(d, r) = 2 * sqrt(pow(d / 2, 2) - pow(r, 2));
pillar_diam = nut_diam + 2 * tol + wall_thick;
pillar_at_radius = (ball_diam - 2 * wall_thick - pillar_diam) / 2;
height_at_pillar = height_at_radius(ball_diam, pillar_at_radius);
catch_offset = pillar_at_radius;
echo(pillar_diam=pillar_diam, pillar_at_radius=pillar_at_radius, height_at_pillar=height_at_pillar, catch_offset=catch_offset);

//engraving variables
chars = "MAKERS MAKING CHANGE";
chars2 = "MAKERSMAKINGCHANGE.COM";
radius = (ball_diam/2)-3;
myPi = 3.14159;
chars_per_circle = 40;
step_angle = 360 / chars_per_circle;
circumference = 2 * PI * radius;
char_size = circumference / chars_per_circle;
char_thickness = 1;

module inprofile() {
    // rather than using a sphere, rotate_extrude a 2D path
    offset(r=-3 * wall_thick/2, $fn=16)difference() {
        circle(d=ball_diam, center=true, $fn=32);
        translate([-(ball_diam-(pen_diam + tol))/2, 0])square(ball_diam, center=true);
    }
}

module profile() {
    // 2D path for profile; looks like a letter D, kinda
    union() {
        difference() {
            offset(r=3 * wall_thick / 2, $fn=16)inprofile();
            offset(r=wall_thick / 2, $fn=16)inprofile();
        }
        translate([ball_diam / 2 - wall_thick, 0])square(wall_thick, center=true);
    }
}

module pillars() {
    // solid pillars we shoot the screw/nut holes through
    for(i=[0:2]) {
        rotate([0, 0, i * 120])translate([pillar_at_radius, 0, 0])cylinder(d=pillar_diam, h=2*height_at_pillar, center=true);
    }
}
            
module stiffeners() {
    // pen pipe stiffeners: two, 120 deg apart
    for(i=[0:1]) {
        rotate([0,0,30 + i * 120])rotate([-90, 0, 0])translate([0, 0, (pen_diam + wall_thick)/2])cylinder(d=screw_nom_diam, h=pillar_at_radius);
    }
}

module catch_reinforce() {
    // this is ugly: make a block to take pen-holding screw/nut
    //  but angled so you can print without support
    rotate([90, 0, 0])linear_extrude(height=pillar_diam, center=true)polygon([
    [ pen_diam / 2, catch_offset ],
    [ pen_diam / 2, catch_offset - pillar_diam / 2],
    [ pillar_at_radius, 0 ],
    [ pen_diam / 2, -(catch_offset - pillar_diam / 2)],
    [ pen_diam / 2, -catch_offset ],
    [ pen_diam / 2, -ball_diam/2 ],
    [ ball_diam/2, -ball_diam/2 ],
    [ ball_diam/2, ball_diam/2 ],
    [ pen_diam / 2, ball_diam/2 ],
    ]);
}

module inside_bits() {
    // all of the interior detail, clipped to the outer shell size
    intersection() {
        union() {
            stiffeners();
            pillars();
            catch_reinforce();
        }
        rotate_extrude()offset(r=wall_thick, $fn=16)inprofile();
    }
}

module screw_holes() {
    // three holes around edge: these are negative spaces
    // nut holes have six sides ('cylinder ... $fn=6') as
    // we emulate hex nuts that way: low-poly cylinders!
    for(i=[0:2]) {
        translate([pillar_at_radius * cos(i * 120), pillar_at_radius * sin(i * 120), 0]) {
            cylinder(d=screw_nom_diam + tol, h=ball_diam, center=true, $fn=32);
            translate([0, 0, pillar_height/2])rotate([0, 0, 30])cylinder(d=nut_diam + tol, h=ball_diam, $fn=6);
            translate([0, 0, -1*(ball_diam + pillar_height/2)])cylinder(d=screw_head_diam + tol, h=ball_diam, $fn=32);
        }
    }
}

module nut_catches() {
    // negative space for pen grip screw holes and nut catches
    // top screw hole
    translate([0, 0, catch_offset])rotate([90, 0, 90])union() {
        cylinder(d=screw_nom_diam + tol, h=ball_diam, $fn=32);
        translate([0,0,screw_length+1])cylinder(d=screw_head_diam + tol, h=ball_diam, $fn=32);
        // top nut catch
        translate([0,0,(pen_diam + tol + wall_thick) / 2])hull() {
            rotate([0, 0, 30])cylinder(d=nut_diam + tol, h=nut_thick + tol, $fn=6);
            translate([0, -ball_diam / 2, 0])rotate([0, 0, 30])cylinder(d=nut_diam + tol, h=nut_thick + tol, $fn=6);
        }
    }
    // bottom screw hole
    translate([0, 0, -catch_offset])rotate([90, 0, 90])union() {
        cylinder(d=screw_nom_diam + tol, h=ball_diam, $fn=32);
        translate([0,0,screw_length+1])cylinder(d=screw_head_diam + tol, h=ball_diam, $fn=32);
        // bottom nut catch
        translate([0,0,(pen_diam + tol + wall_thick) / 2])hull() {
            rotate([0, 0, 30])cylinder(d=nut_diam + tol, h=nut_thick + tol, $fn=6);
            translate([0, ball_diam / 2, 0])rotate([0, 0, 30])cylinder(d=nut_diam + tol, h=nut_thick + tol, $fn=6);
        }
    }
}

module shell() {
    // assemble all the things!
    difference() {
        union() {
            // the positive bits
            rotate_extrude()profile();  // outer shell
            inside_bits();              // interior detail
			}
			//engraving text
			for(i = [0 : chars_per_circle - 1]) {
    rotate(i * step_angle) 
        translate([0, radius + char_size / 2, 3]) 
            rotate([90, 0, 180]) linear_extrude(char_thickness) text(
                chars[i], 
                font = "Courier New; Style = Bold", 
                size = char_size, 
                valign = "center", halign = "center"
            );
        }//for (end engraving)
        union() {
            // the negative bits
            screw_holes();              // edge holes
            nut_catches();
        }
    }
}

module slice() {
    // split ball across middle and place halves side by side
    // (lower half flipped) for easy printing
    union() {
        translate([-(ball_diam + pen_diam) / 2, 0, 0]) {
            difference() {
                shell();
                translate([0, 0, -0.6 * ball_diam])cube(1.2 * ball_diam, center=true);
                			//engraving text
			for(i = [0 : chars_per_circle - 1]) {
    rotate(i * step_angle) 
        translate([0, radius + char_size / 2, 3]) 
            rotate([90, 0, 180]) linear_extrude(char_thickness) text(
                chars[i], 
                font = "Courier New; Style = Regular", 
                size = char_size, 
                valign = "center", halign = "center"
            );
        }//for (end engraving)
				}
        }
        translate([(ball_diam + pen_diam) / 2, 0, 0]) {
            difference() {
                rotate([180, 0, 0])shell();
                translate([0, 0, -0.6 * ball_diam])cube(1.2 * ball_diam, center=true);
							//engraving text
			for(i = [0 : chars_per_circle - 1]) {
    rotate(i * step_angle) 
        translate([0, radius + char_size / 2, 3]) 
            rotate([90, 0, 180]) linear_extrude(char_thickness) text(
                chars2[i], 
                font = "Courier New; Style = Bold", 
                size = char_size, 
                valign = "center", halign = "center"
            );
        }//for (end engraving)
            }
        }
    }
}

slice(); // generate the sliced module

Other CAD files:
Palm-Pen-Holder/Build_Files/3D_Print_ Files/Med_Palm_Pen_Large_Pen_hole.stl
Pen-Ball/Build_Files/3D_Print_Files/Medium_Pen_ball_Small_Pen_hole.stl
Reading-Bar-Flat/Build_Files/3D_Print_Files/Reading_Bar_Flat_Small_Window.STL
Bottle-Opener/Build_Files/Bottle_Opener_30.stl
Bottle-Opener/Build_Files/Bottle_Opener_35.stl
Bottle-Opener/Build_Files/Bottle_Opener_40.stl
Dice-Roller/Build_Files/3D_Print_Files/Rumble_Plate_STLs/Rumble_Plate_Button.stl
Dice-Roller/Build_Files/3D_Print_Files/Rumble_Plate_STLs/Rumble_Plate_Lid.stl
Dice-Roller/Build_Files/3D_Print_Files/Rumble_Plate_STLs/Rumble_Plate_Plate.stl
Dice-Roller/Build_Files/3D_Print_Files/Rumble_Plate_STLs/Rumble_Plate_Retaining_Ring.stl
Dice-Roller/Build_Files/3D_Print_Files/Vertical_Push_Base_STLs/Vertical_Push_Base_lever.stl
Dice-Roller/Build_Files/3D_Print_Files/Vertical_Push_Base_STLs/Vertical_Push_Base_top.stl
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

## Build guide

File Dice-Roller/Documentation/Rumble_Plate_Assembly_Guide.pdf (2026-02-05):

V2.0 | <September> <2021>

## Rumble Plate

## ASSEMBLY GUIDE

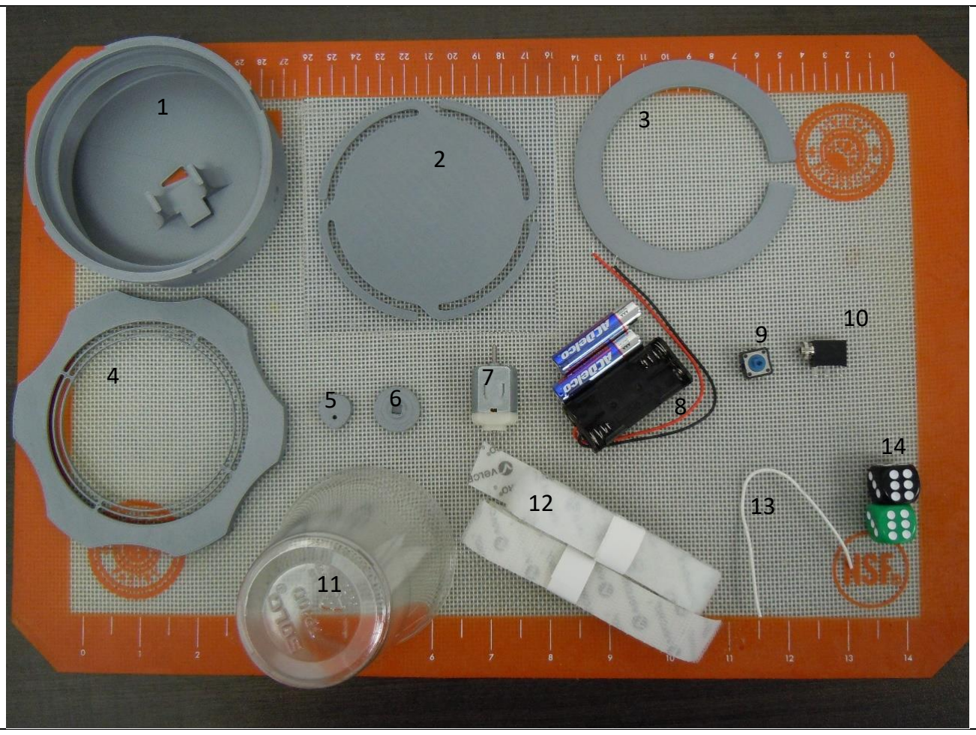
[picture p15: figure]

© 2021 by <Author>. This work is licensed under the CC BY SA 4.0 License: http://creativecommons.org/licenses/by-sa/4.0
Files available at <Replace with MMC Library Link> | Page 1 of 14

### Required Components

BOM
1. 3D printed Base
2. 3D printed Plate
3. 3D printed
Retaining Ring
4. 3D printed Lid
5. 3D printed Cam
6. 3D printed Button
7. 130 size DC motor
8. 2x AAA Battery
Holder (and 2
AAA batteries)
9. Omron B50503F
Switch
10. 3.5mm Jack
11. Clear Plastic Cup
12. Velcro
13. Wire
14. Dice
15. Optional: 3D
printed Vertical
Push Base parts

### Required Tools

- Super Glue (and/or hot glue)
- 3D printer
- Soldering Iron
- Wire Strippers
- Pliers
- Extra wire
- Knife

### Required Personal Protective Equipment (PPE)

- Safety Glasses

V2.0 | <September> <2021>

## Rumble Plate

## ASSEMBLY GUIDE

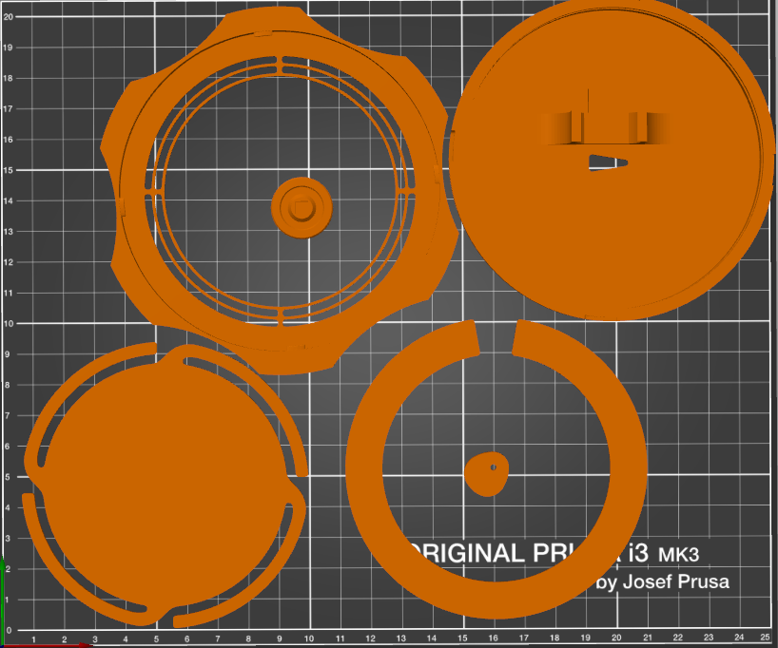
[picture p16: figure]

Files available at <Replace with MMC Library Link> | Page 2 of 14

### Assembly Instructions

### Step 1

Setting up the 3D prints:

All STLs are oriented in the correct printing position. For an ideal print time, a layer height of 0.3 mm and 20% infill is recommended for all parts. If you desire a nicer finish, 0.2 mm is also ok, but will increase the print time. This is most noticeable for the Base.

All the prints can fit on a Prusa i3 MK3 print bed if arranged nicely, otherwise, some must be printed separately.

V2.0 | <September> <2021>

## Rumble Plate

## ASSEMBLY GUIDE

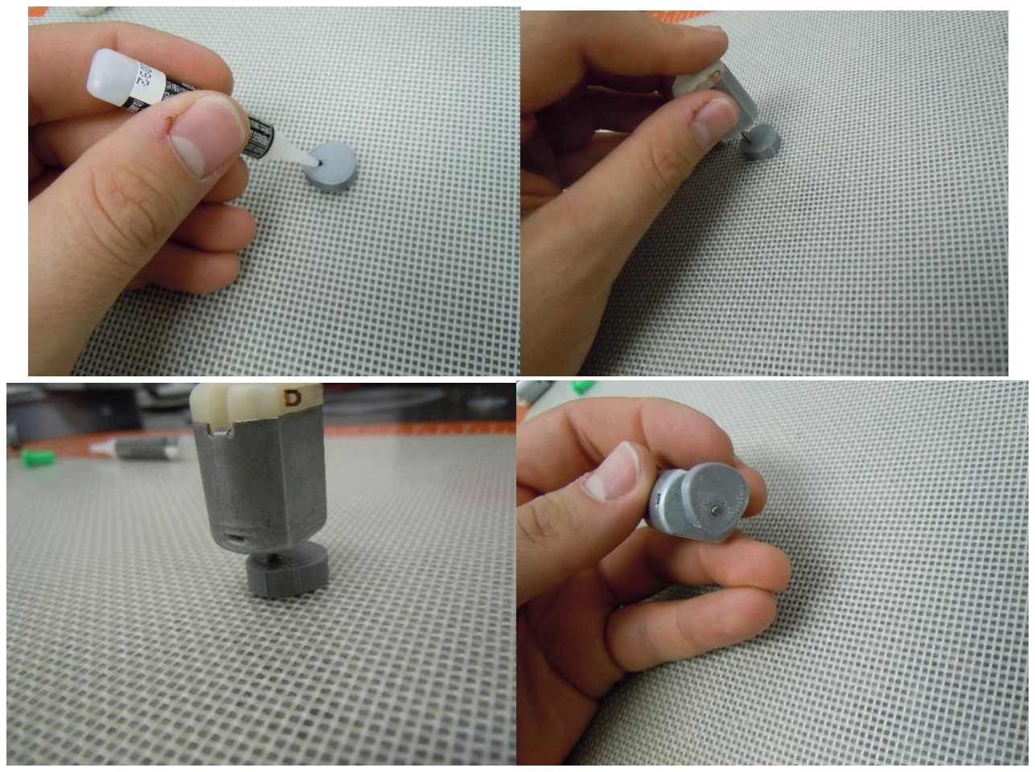
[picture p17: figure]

Files available at <Replace with MMC Library Link> | Page 3 of 14

### Step 2

Fitting the cam to the motor shaft:

Place 2-3 drops of super glue into the hole on the cam, careful not to let it drip fully through. Place the cam lying on its flat side and press the motor shaft into the hole until it is flush with the opposite side. Place the motor on its side (the flat) to allow the glue to dry. Note: Important not to let super glue drip into the motor and to make sure the shaft ends up flush with the face of the cam.

V2.0 | <September> <2021>

## Rumble Plate

## ASSEMBLY GUIDE

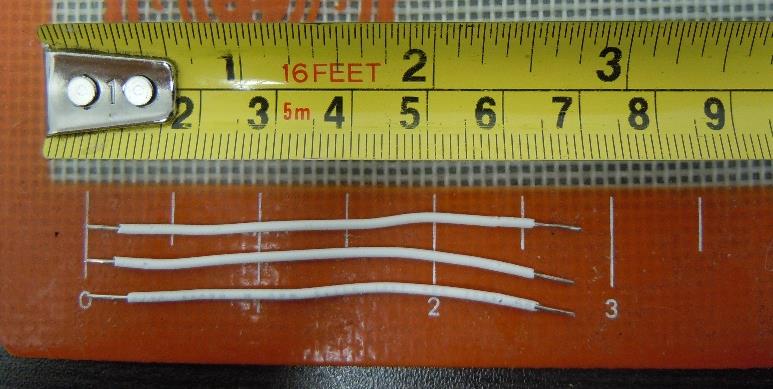
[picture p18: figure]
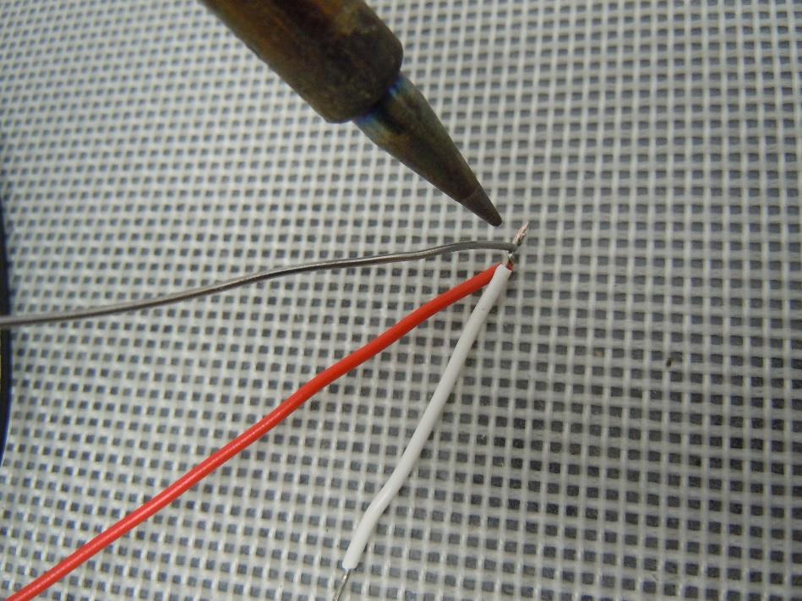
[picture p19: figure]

Files available at <Replace with MMC Library Link> | Page 4 of 14

### Step 3

Soldering the motor jack, and battery holder:

Cut three 7 cm lengths of wire and strip 1cm off both ends of each:

Solder one of these lengths to the red wire of the battery holder:

V2.0 | <September> <2021>

## Rumble Plate

## ASSEMBLY GUIDE

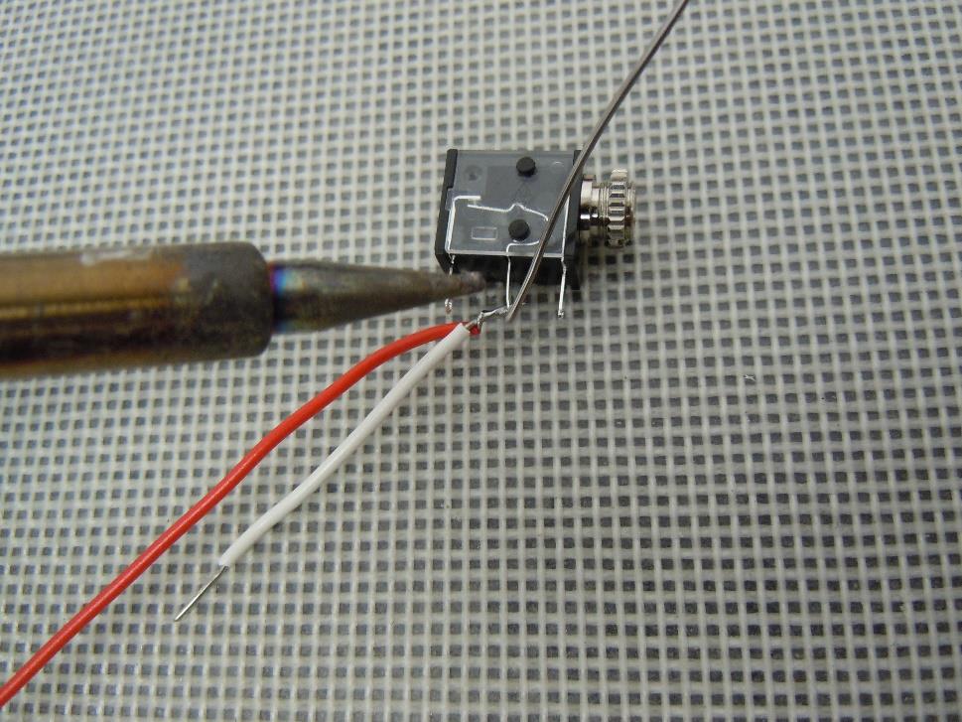
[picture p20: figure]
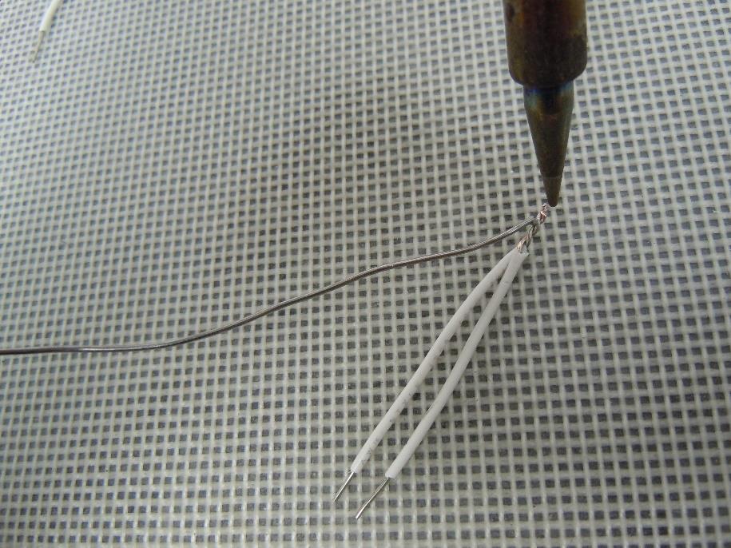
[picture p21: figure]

Files available at <Replace with MMC Library Link> | Page 5 of 14

Solder these connected wires to the middle prong of the jack:

Solder the other two 7 cm wires together as shown:

V2.0 | <September> <2021>

## Rumble Plate

## ASSEMBLY GUIDE

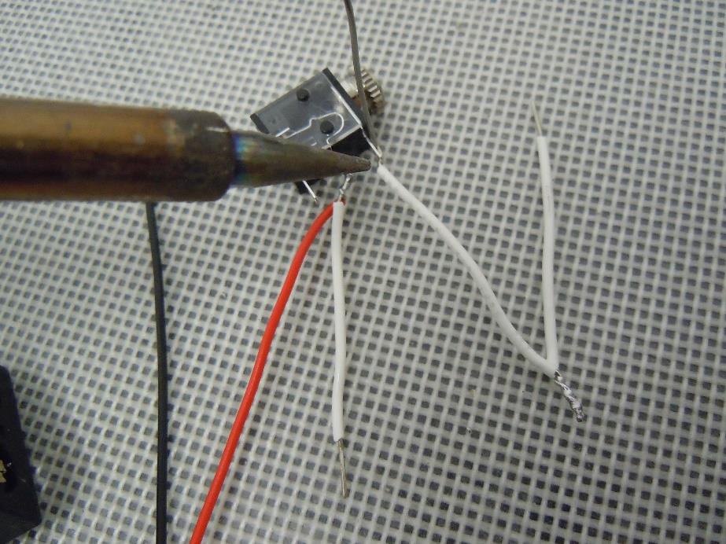
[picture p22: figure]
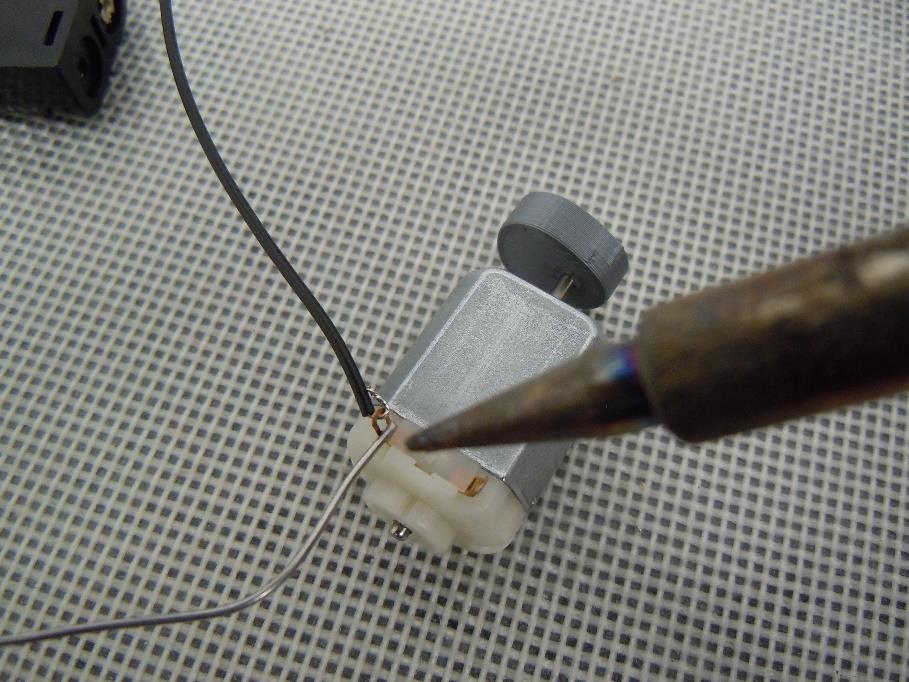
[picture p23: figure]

Files available at <Replace with MMC Library Link> | Page 6 of 14

Solder one single end of the connected wires to the prong closest to the jack input:

Solder the black wire of the battery holder to a motor prong:

V2.0 | <September> <2021>

## Rumble Plate

## ASSEMBLY GUIDE

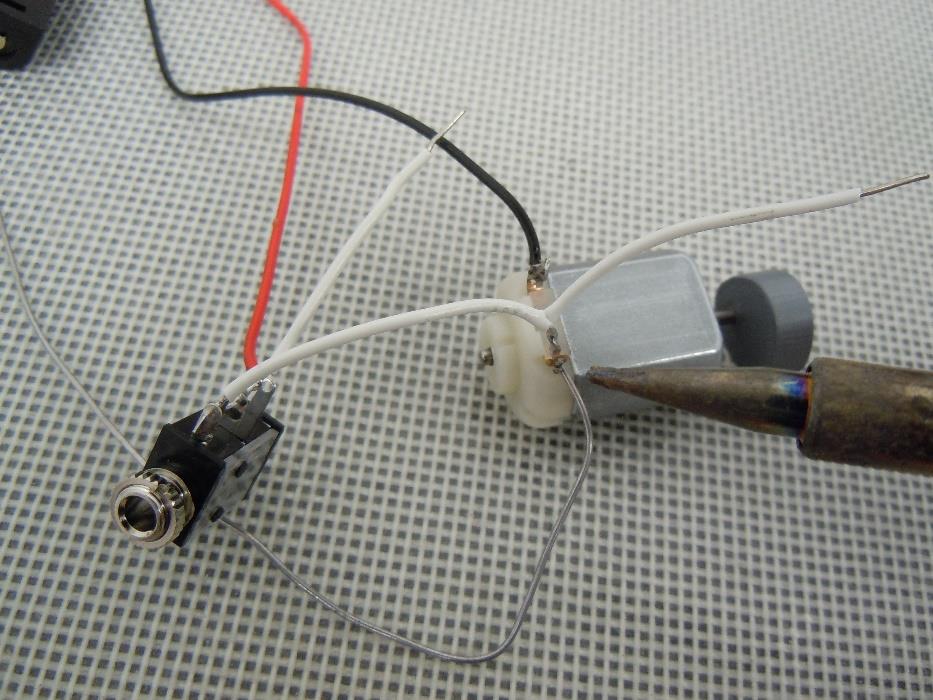
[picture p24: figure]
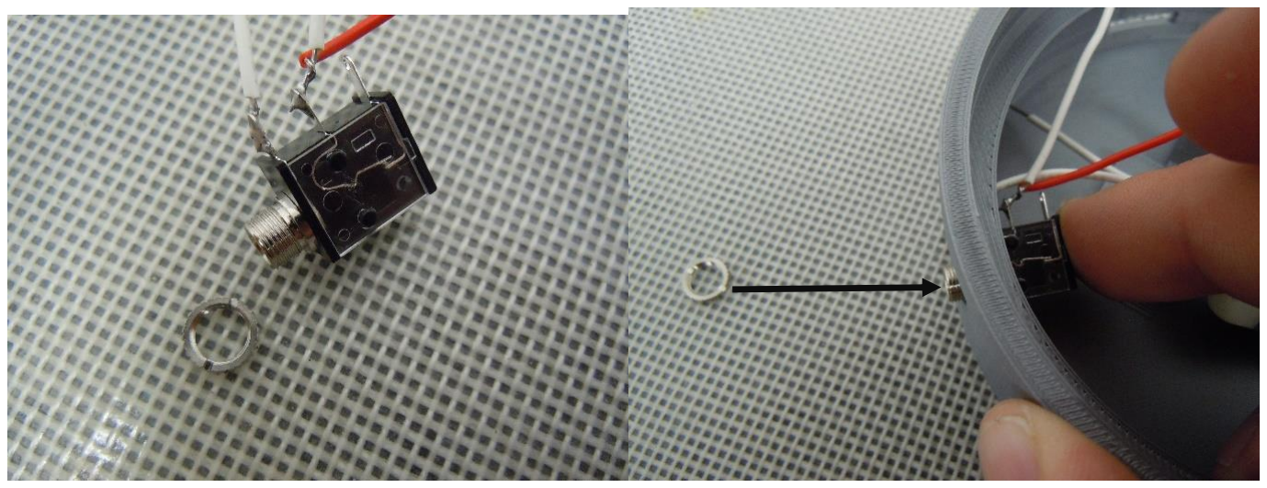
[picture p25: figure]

Files available at <Replace with MMC Library Link> | Page 7 of 14

Solder the connected section of the two 7 cm wires to the other motor prong:

Insert batteries into the holder and test the circuit. (input switch into jack and touch switch wires together)

### Step 4

Securing the soldered parts into the base:

Remove the nut from the jack and insert through the circular hole with the prongs pointed to the switch mount opposite, re-screw the nut back on and tighten with pliers:

## Rumble Plate

## ASSEMBLY GUIDE

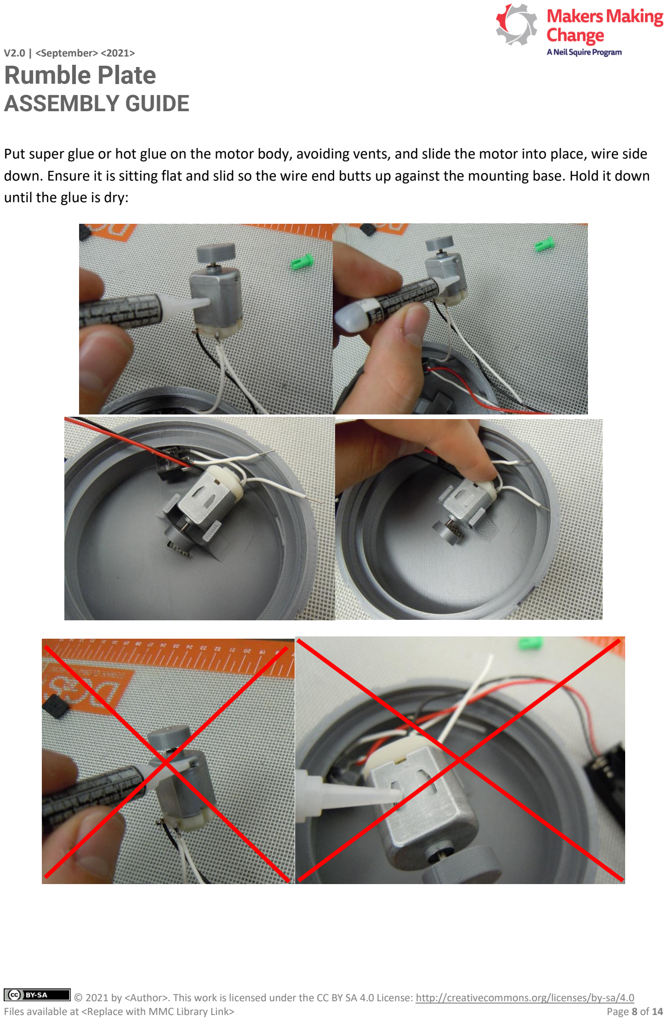
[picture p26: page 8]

V2.0 | <September> <2021>
Files available at <Replace with MMC Library Link> | Page 8 of 14

Put super glue or hot glue on the motor body, avoiding vents, and slide the motor into place, wire side down. Ensure it is sitting flat and slid so the wire end butts up against the mounting base. Hold it down until the glue is dry:

V2.0 | <September> <2021>

## Rumble Plate

## ASSEMBLY GUIDE

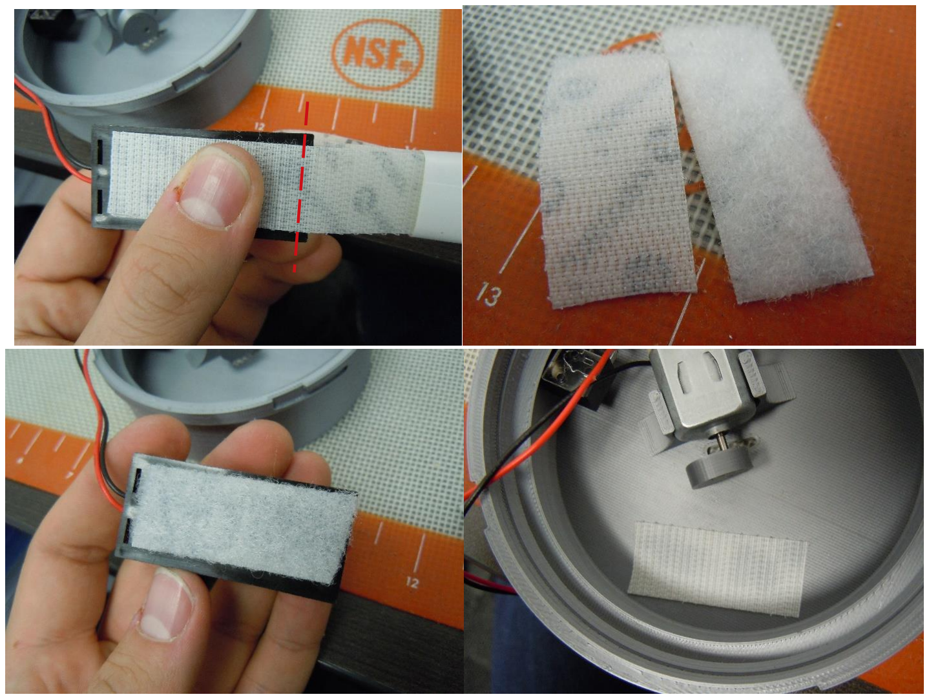
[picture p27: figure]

Files available at <Replace with MMC Library Link> | Page 9 of 14

Glue opposite patches of Velcro to the backside of the battery holder and to the floor of the base:

Note: Some Velcro is self-adhering, in which case, glue is not necessary.

Note: Put the hook, or scratchy, section of Velcro on the base itself.

V2.0 | <September> <2021>

## Rumble Plate

## ASSEMBLY GUIDE

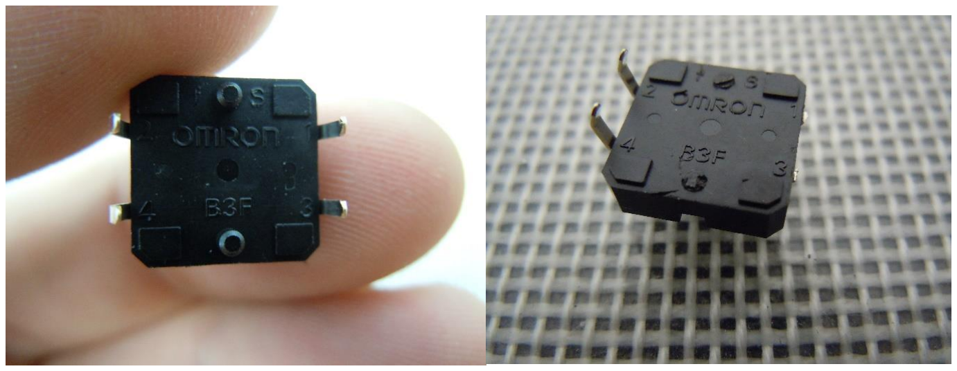
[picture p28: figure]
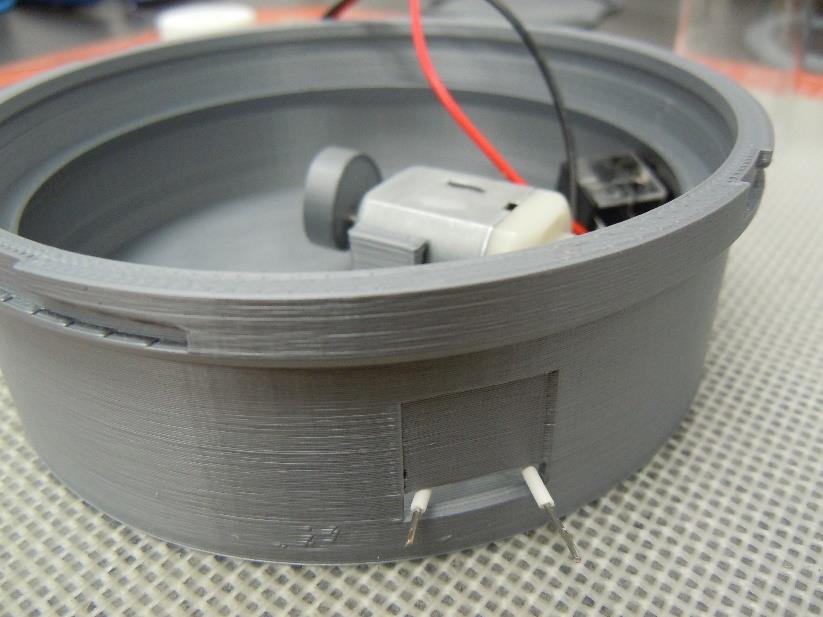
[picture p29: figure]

Files available at <Replace with MMC Library Link> | Page 10 of 14

### Step 5

Soldering the switch:

Cut the prongs off one side off the switch using wire cutters and cut the cylinders off the back of the switch (Note: You can use a knife to make the bottom smoother):

Take the two unused wire ends and poke them out the rectangular hole in the base sidewall:

V2.0 | <September> <2021>

## Rumble Plate

## ASSEMBLY GUIDE

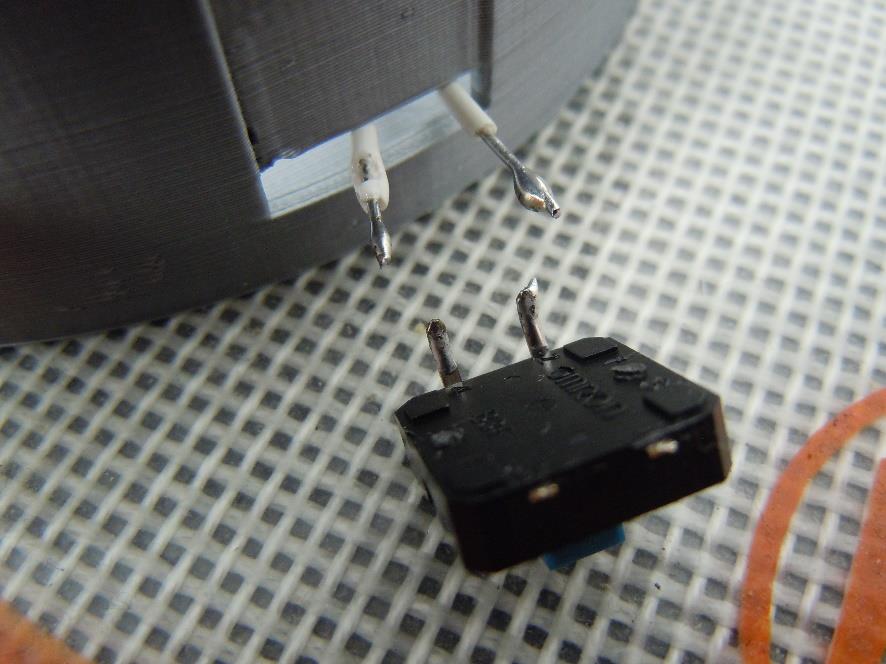
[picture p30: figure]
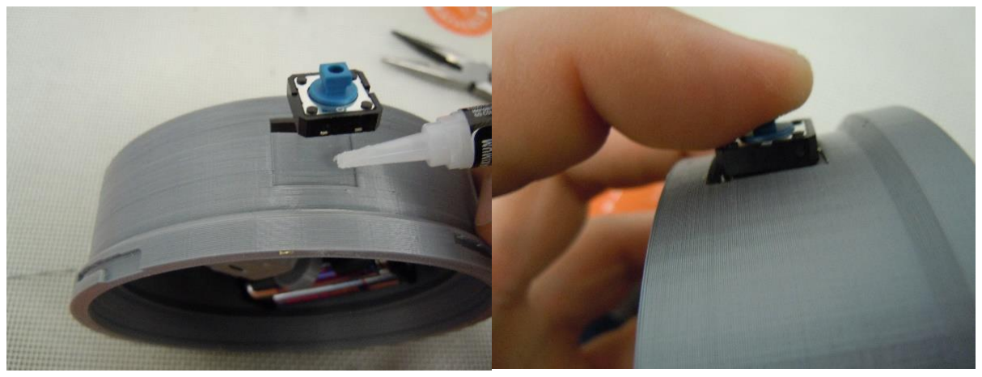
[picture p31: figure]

Files available at <Replace with MMC Library Link> | Page 11 of 14

Tack some solder onto both wire ends and to the switch prongs and proceed to solder one wire to each prong, respectively:

### Step 6

Assembling the remaining parts:

Glue the switch onto the base sidewall:

V2.0 | <September> <2021>

## Rumble Plate

## ASSEMBLY GUIDE

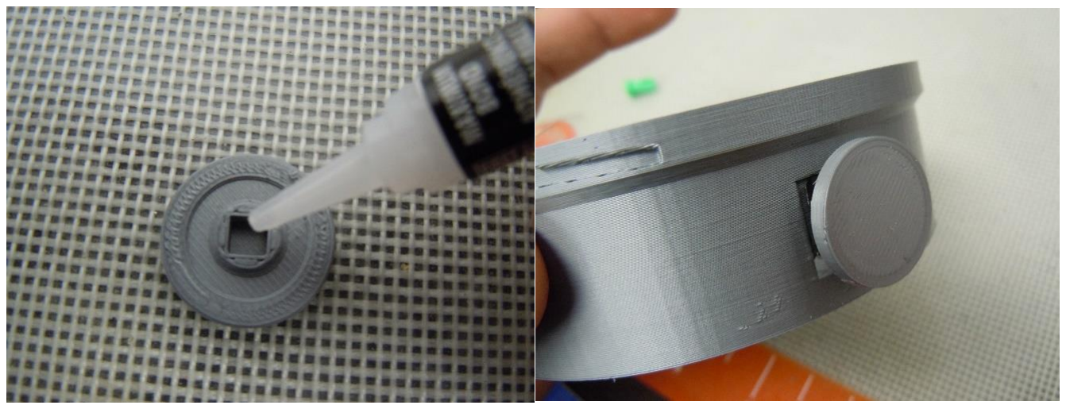
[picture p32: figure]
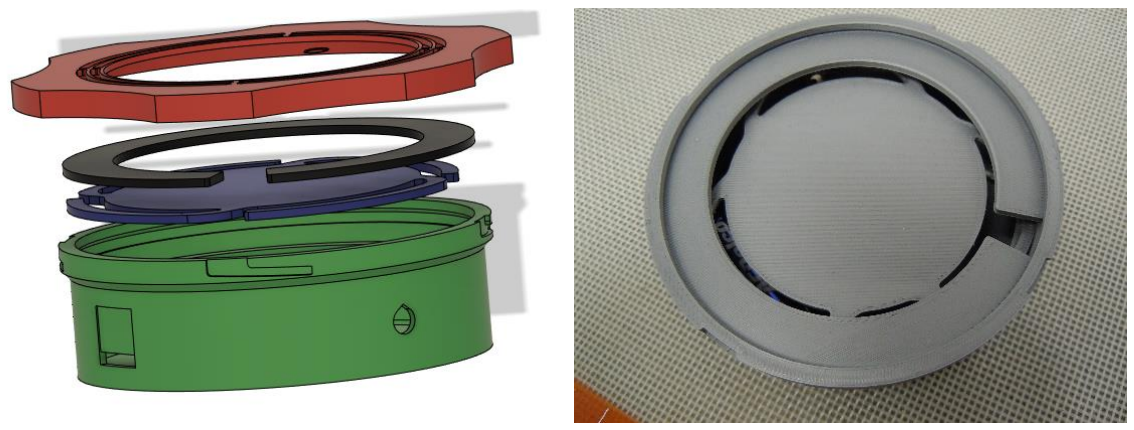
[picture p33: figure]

Files available at <Replace with MMC Library Link> | Page 12 of 14

Glue the button cap onto the switch, careful not to let any glue drip into the switch:

Place the plate down, and then insert the retaining ring:

Note: Ensure the retaining ring is in the groove cut out along the inside and not dropped down past it.

V2.0 | <September> <2021>

## Rumble Plate

## ASSEMBLY GUIDE

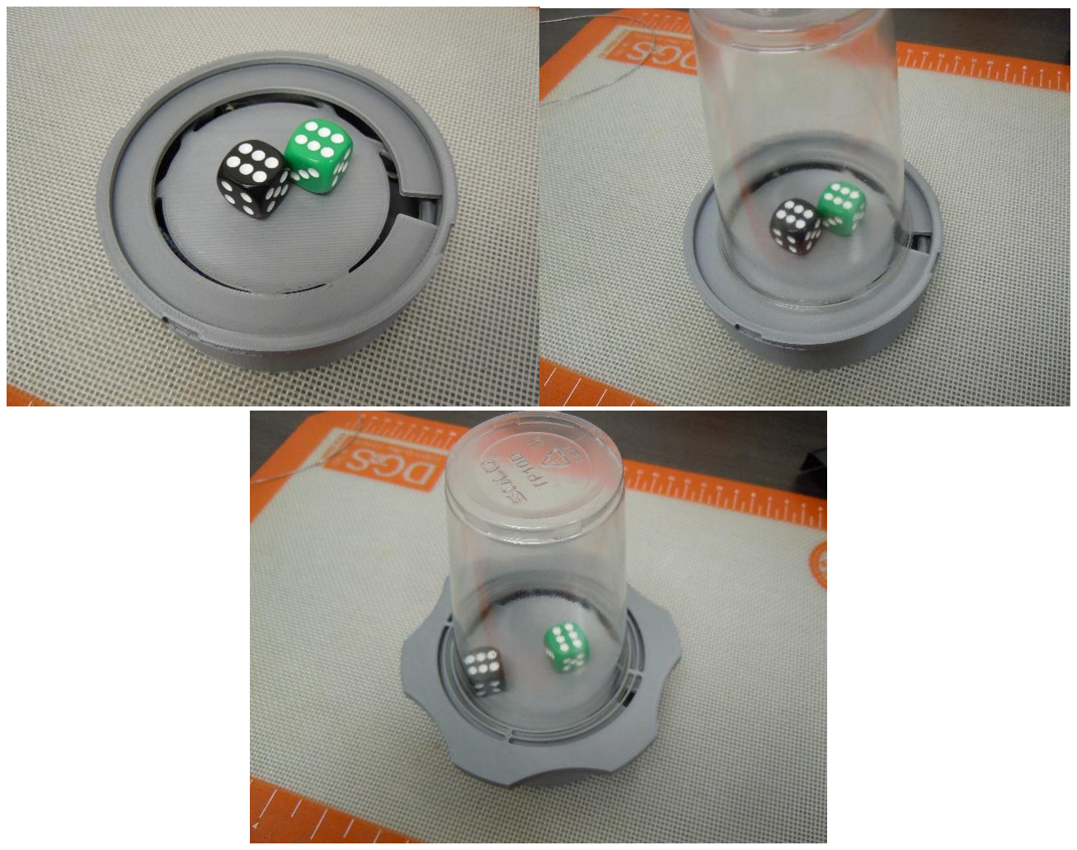
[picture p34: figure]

Files available at <Replace with MMC Library Link> | Page 13 of 14

Add in some dice on top of the plate, place your cup over, and then twist on the lid.

V2.0 | <September> <2021>

## Rumble Plate

## ASSEMBLY GUIDE

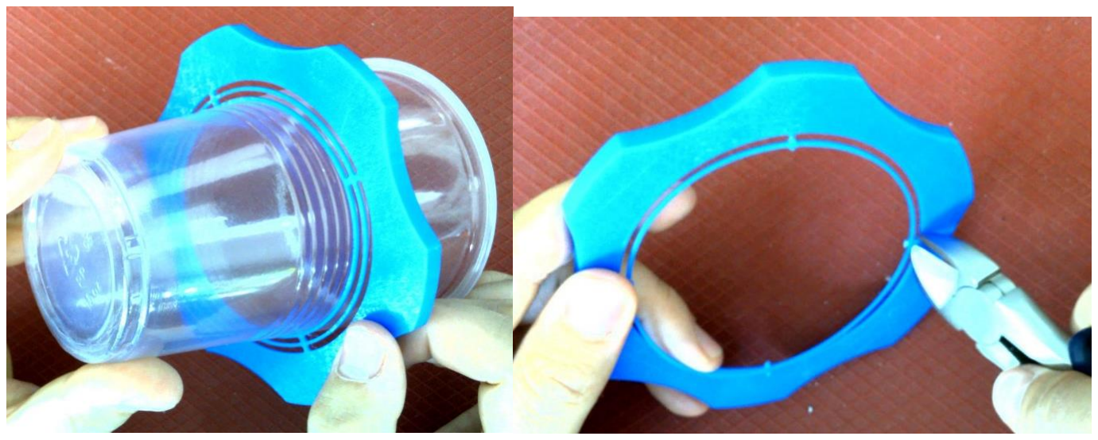
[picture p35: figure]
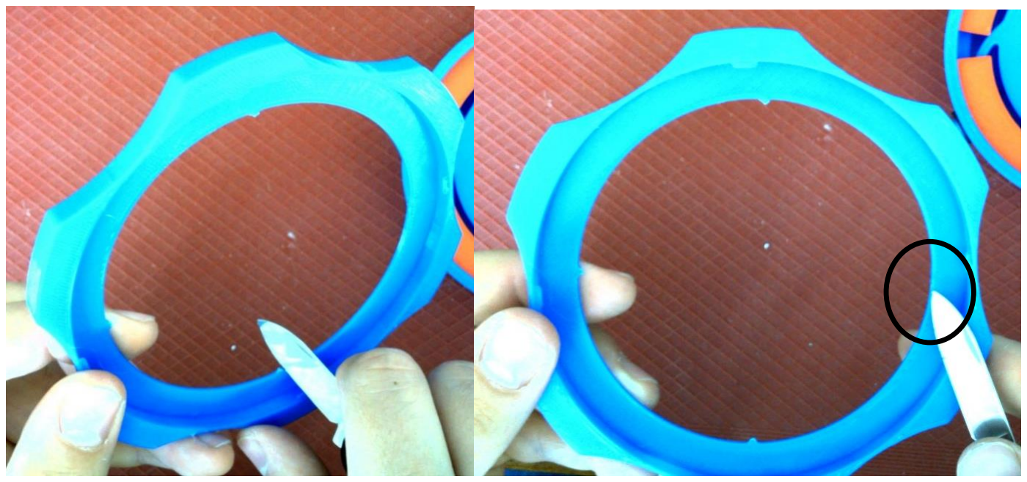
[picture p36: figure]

Files available at <Replace with MMC Library Link> | Page 14 of 14

Note: If the cup diameter is larger than the inner diameter of the lid, carefully cut the inner ring out of the lid. You can use a pair of wire cutters or a knife. The knife will help smooth the edges. If the cup diameter is still slightly too large, you can trim the lip of the cup off carefully with a knife or scissors until the cup rim fits in the lid diameter.

Be careful with the sharp knife!

If the cup is still too large, you can carefully trim down the rim until it fits when the lid is twisted onto the base.

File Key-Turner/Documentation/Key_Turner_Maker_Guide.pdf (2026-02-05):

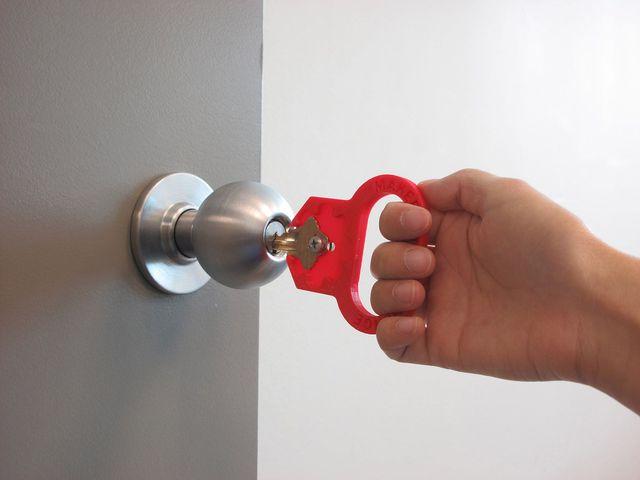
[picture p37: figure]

0.80 hrs

1 pcs

f

0.20 mm

k

0.40 mm

h

PLA

10 g

d

Prusa

MK3/S/S+

# Summary

Accessory for people with limited finger dexterity to hold keys.

Household (https://printables.com/model?categoryId=3) | > | Other House Equipment (https://printables.com/model?categoryId=45)
Tags: | hand | keychain | key | disability | arthritis
assistivetechnology | assistivedevice

The key turner is a low-cost, 3D-printed handheld tool for people with

arthritis or other disabilities to operate their keys.

Users loop their finger through the hole and twist to lock and unlock doors

with minimal wrist movement. The large key bed can accommodate

various shape of key heads.

### Print Settings

### Infill: 50%

Makers Making Change (https://printables.com/@MakersMakingChange)

# Key Turner

### VIEW IN BROWSER (https://printables.com/model/213712-key-turner)

updated 29. 8. 2023 | published 29. 8. 2023

# Model files

### Resolution: 0.2mm

### Supports: No

### Rafts: No

### Hardware Required:

1 M4 x 12mm screw (metric) / #8 - 1/2" screw (imperial)

1 M4 hex nut / #8 hex nut

2 M4 washer /#8 washer

### About Makers Making Change

Makers Making Change (https://makersmakingchange.com/) is an initiative of the Neil Squire Society, a

Canadian non-profit that empowers people with disabilities through

technology.

We leverage the capacity of community based Makers, (https://makersmakingchange.com/learn-how-our-community-works/) Disability

Professionals and Volunteers to develop and deliver affordable Open

Source Assistive Technologies. (https://makersmakingchange.com/assistive-devices/)

Volunteer (https://makersmakingchange.com/maker-wanted/) to print a device

Tackle (https://makersmakingchange.com/forum/forums/design-challenges/) a design challenge

Submit (https://makersmakingchange.com/submit-an-idea/) an assistive device idea

Follow us on Instagram, (https://www.instagram.com/makersmakingchange/) Facebook, (https://www.facebook.com/makersmakechange/) and Twitter (https://twitter.com/makermakechange)

•

•

•

key_turner.stl

# Print files

h PLA | k 0.40 mm | f 0.20 mm | 0.80 hrs | 10 g | d Prusa MK3/S/S+

# License

This work is licensed under a

Creative Commons (4.0 International License)

Attribution-ShareAlike (http://creativecommons.org/licenses/by-sa/4.0/)

### ✖ | Sharing without ATTRIBUTION

✔ | Remix Culture allowed
✔ | Commercial Use
✔ | Free Cultural Works
✔ | Meets Open Definition

key_turner_02mm_pla_mk3s_48m.gcode

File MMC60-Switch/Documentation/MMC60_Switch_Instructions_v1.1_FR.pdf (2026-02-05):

# Commutateur MMC60

# GUIDE DE MONTAGE

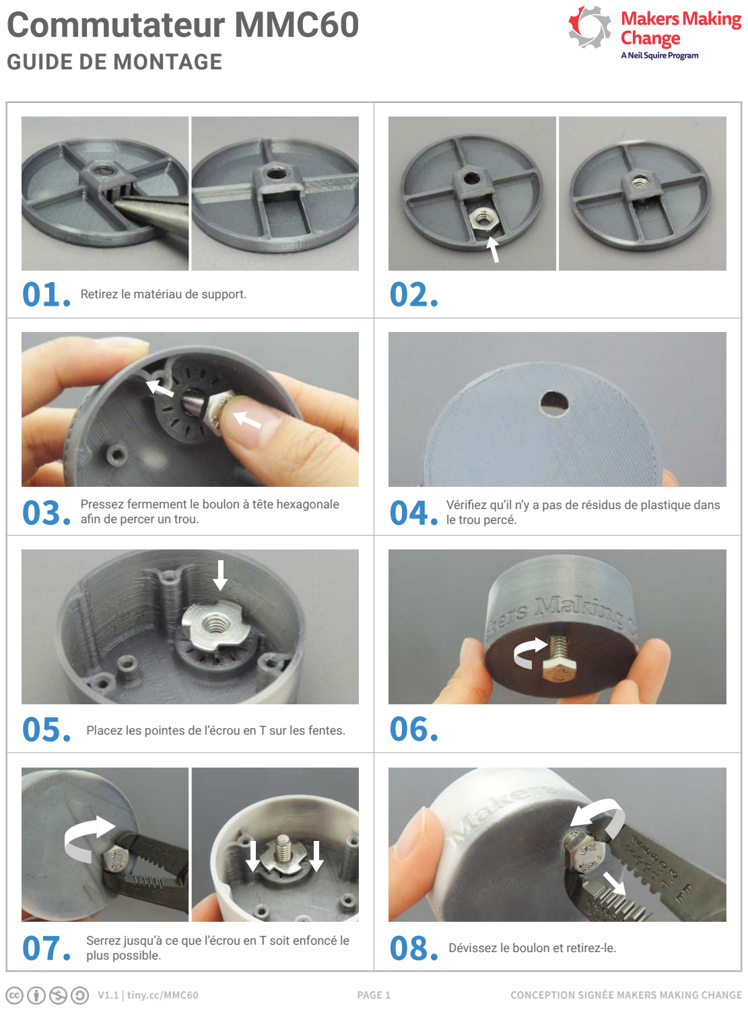
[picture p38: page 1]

02.

07.

03.

06.

04.

08.

PAGE 1 | CONCEPTION SIGNÉE MAKERS MAKING CHANGE

### FRONT

### BACK

Vérifiez qu’il n’y a pas de résidus de plastique dans le trou percé.

Pressez fermement le boulon à tête hexagonale afin de percer un trou.

Retirez le matériau de support.

05. Placez les pointes de l’écrou en T sur les fentes.

Serrez jusqu’à ce que l’écrou en T soit enfoncé le
plus possible. | Dévissez le boulon et retirez-le.
V1.1 | tiny.cc/MMC60

01.

# Commutateur MMC60

# GUIDE DE MONTAGE

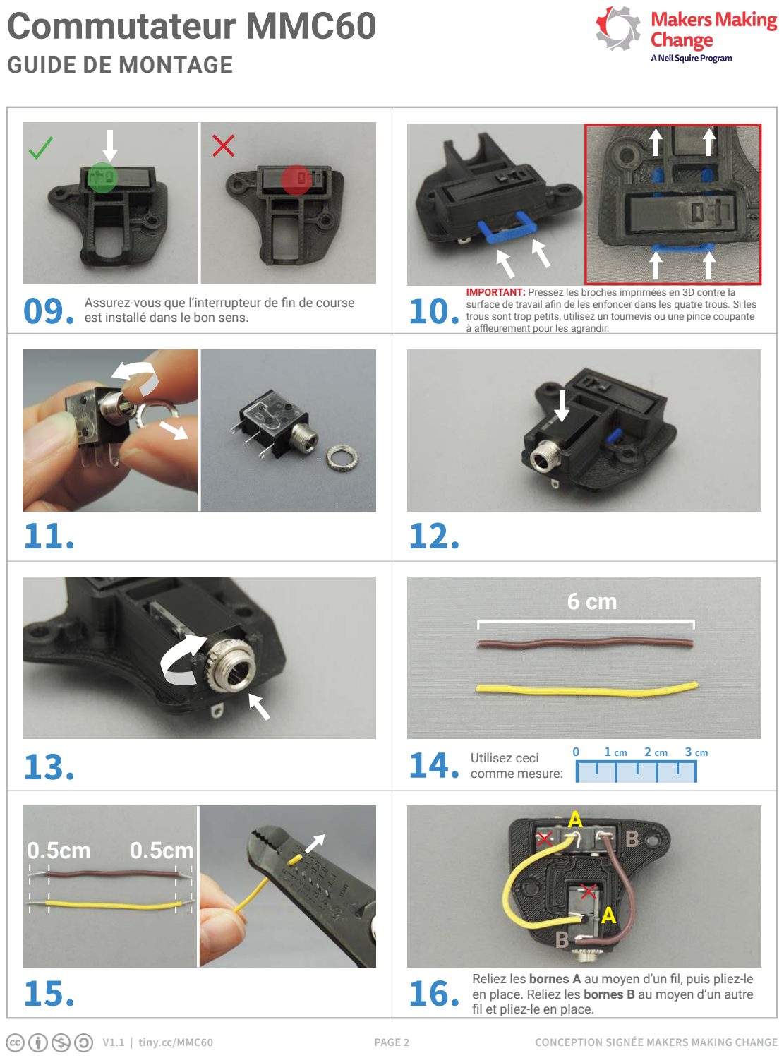
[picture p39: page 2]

12.

14.

16.

11.

13.

15.

10.
IMPORTANT: Pressez les broches imprimées en 3D contre la surface de travail afin de les enfoncer dans les quatre trous. Si les trous sont trop petits, utilisez un tournevis ou une pince coupante à affleurement pour les agrandir.
V1.1 | tiny.cc/MMC60 | PAGE 2 | CONCEPTION SIGNÉE MAKERS MAKING CHANGE

# 6 cm

Utilisez ceci
comme mesure:
0 | 1 cm | 2 cm | 3 cm
0.5cm | 0.5cm

Reliez les bornes A au moyen d’un fil, puis pliez-le en place. Reliez les bornes B au moyen d’un autre fil et pliez-le en place.

A
B

B

A

### 09. Assurez-vous que l’interrupteur de fin de course

est installé dans le bon sens.

# Commutateur MMC60

# GUIDE DE MONTAGE

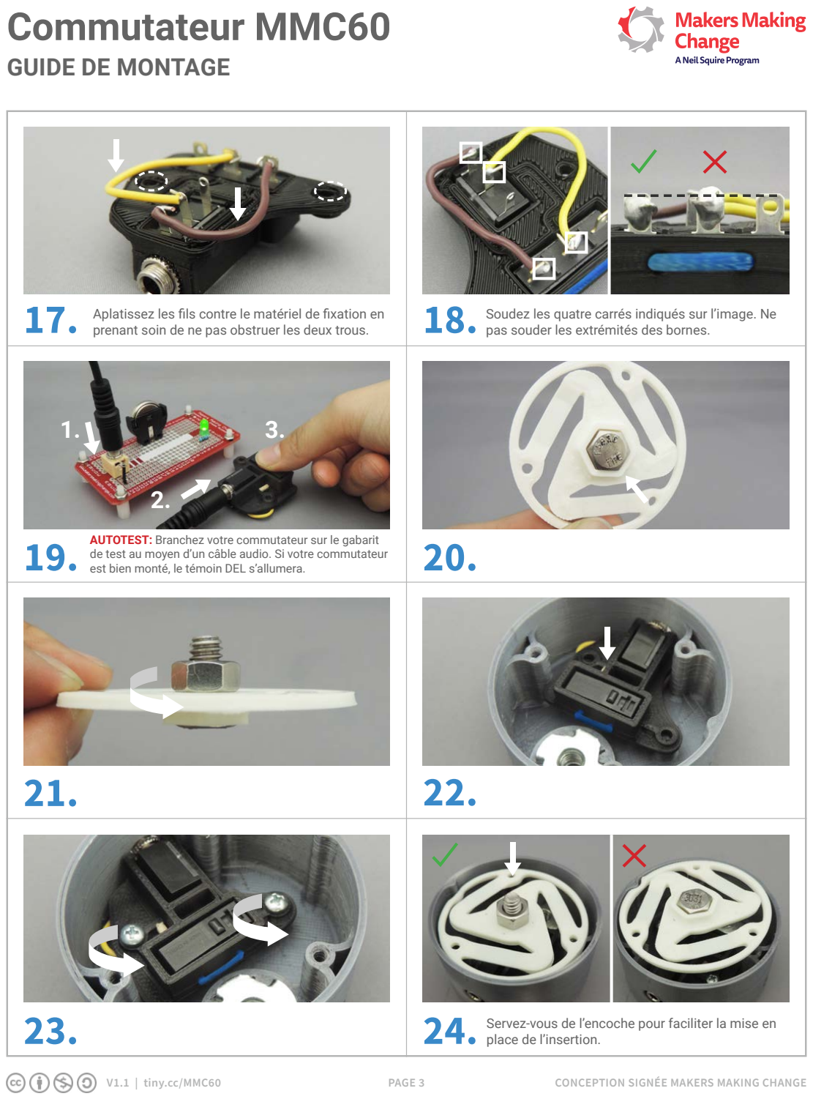
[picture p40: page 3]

18.

23.

17.

19.

22.

20.

24.

### FRONT

### BACK

21.

V1.1 | tiny.cc/MMC60 | PAGE 3 | CONCEPTION SIGNÉE MAKERS MAKING CHANGE

Aplatissez les fils contre le matériel de fixation en prenant soin de ne pas obstruer les deux trous.

Soudez les quatre carrés indiqués sur l’image. Ne pas souder les extrémités des bornes.

AUTOTEST: Branchez votre commutateur sur le gabarit de test au moyen d’un câble audio. Si votre commutateur est bien monté, le témoin DEL s’allumera.

1.

2.

3.

Servez-vous de l’encoche pour faciliter la mise en place de l’insertion.

# Commutateur MMC60

# GUIDE DE MONTAGE

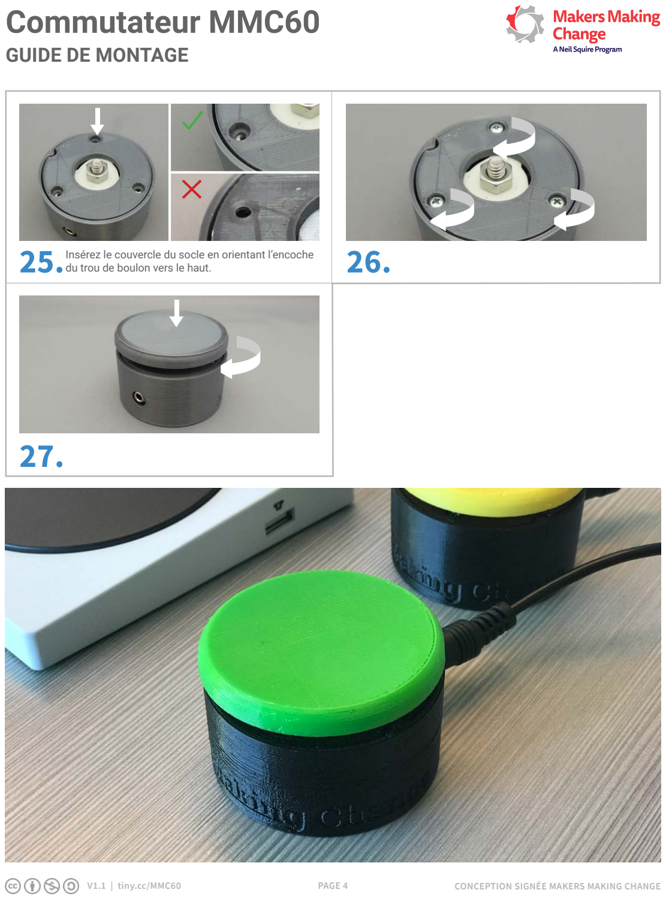
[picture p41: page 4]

25. 26.

27.

V1.1 | tiny.cc/MMC60 | PAGE 4

Insérez le couvercle du socle en orientant l’encoche
du trou de boulon vers le haut.

CONCEPTION SIGNÉE MAKERS MAKING CHANGE

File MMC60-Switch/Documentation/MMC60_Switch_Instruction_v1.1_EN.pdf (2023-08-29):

# MMC60 Switch

# ASSEMBLY MANUAL

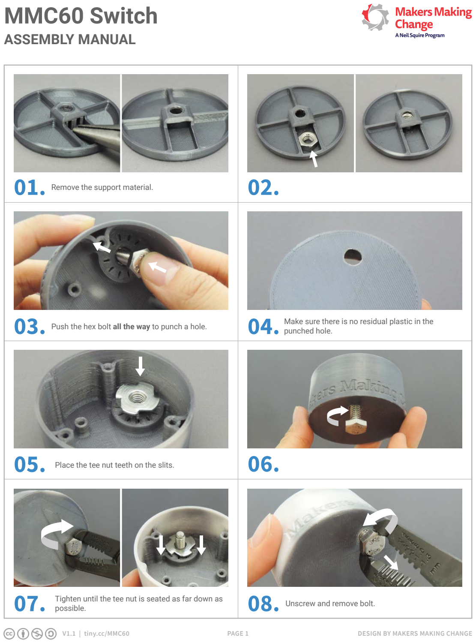
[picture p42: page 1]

02.

07.

03.

06.

04.

08.

PAGE 1 | DESIGN BY MAKERS MAKING CHANGE

### FRONT

### BACK

Make sure there is no residual plastic in the punched hole. Push the hex bolt all the way to punch a hole.

Remove the support material.

05. Place the tee nut teeth on the slits.

Tighten until the tee nut is seated as far down as
possible. | Unscrew and remove bolt.
V1.1 | tiny.cc/MMC60

01.

# MMC60 Switch

# ASSEMBLY MANUAL

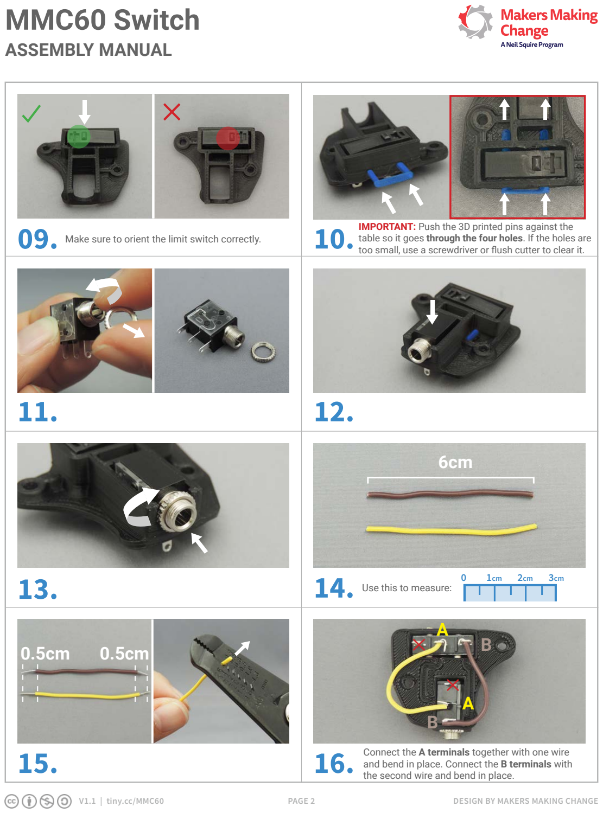
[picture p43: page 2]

12.

14.

16.

11.

13.

15.

09. 10. Make sure to orient the limit switch correctly. IMPORTANT: Push the 3D printed pins against the table so it goes through the four holes. If the holes are too small, use a screwdriver or flush cutter to clear it.
V1.1 | tiny.cc/MMC60 | PAGE 2 | DESIGN BY MAKERS MAKING CHANGE

6cm

Use this to measure:

0 | 1cm | 2cm | 3cm
0.5cm | 0.5cm

Connect the A terminals together with one wire and bend in place. Connect the B terminals with the second wire and bend in place.

A
B

B

A

# MMC60 Switch

# ASSEMBLY MANUAL

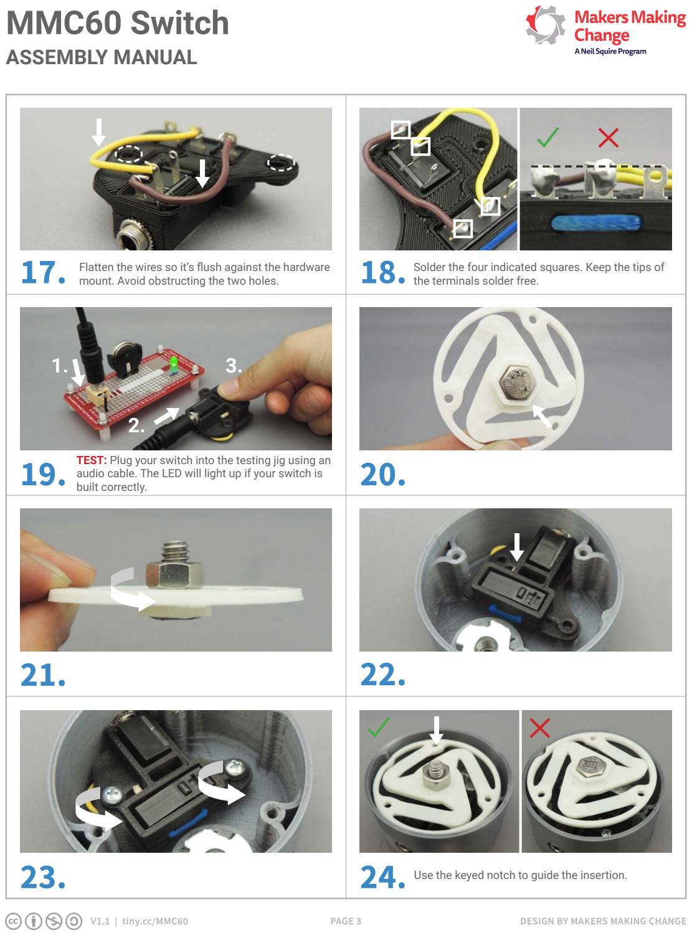
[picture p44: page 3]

18.

23.

17.

19.

22.

20.

24.

### FRONT

### BACK

21.

V1.1 | tiny.cc/MMC60 | PAGE 3 | DESIGN BY MAKERS MAKING CHANGE

Flatten the wires so it’s flush against the hardware mount. Avoid obstructing the two holes.

Solder the four indicated squares. Keep the tips of the terminals solder free.

TEST: Plug your switch into the testing jig using an audio cable. The LED will light up if your switch is built correctly.

1.

2.

3.

Use the keyed notch to guide the insertion.

# MMC60 Switch

# ASSEMBLY MANUAL

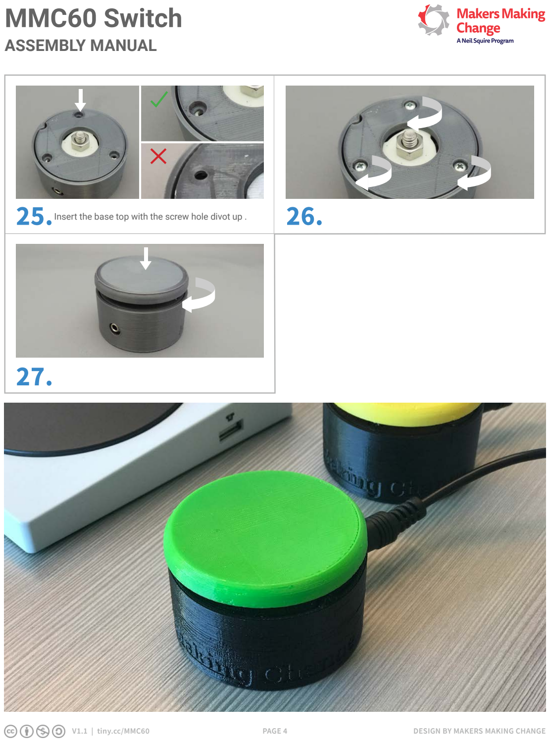
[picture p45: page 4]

25. 26.

27.

V1.1 | tiny.cc/MMC60 | PAGE 4 | DESIGN BY MAKERS MAKING CHANGE

Insert the base top with the screw hole divot up .

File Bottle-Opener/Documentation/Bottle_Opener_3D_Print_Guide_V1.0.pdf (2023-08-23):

V1.0| May 2022

## Bottle Opener

## 3D PRINTING GUIDE

© 2022 by Neil Squire / Makers Making Change. This work is licensed under the CC BY SA 4.0 License: http://creativecommons.org/licenses/by-sa/4.0 Files available at https://makersmakingchange.com/project/bottle-opener/

### 3D Printing Summary

Metrics
Total Print Time (min) | 224 - 241
Total Number of Components | 1 - 5
Typical Total Mass (g) | 36 - 39
Typical Number of Print Setups | 1 - 5

### 3D Printing Settings

Print File Name | Qty | Total Print Time (hr:min) | Mass (g) | Infill (%) | Support | Layer Height/ Nozzle Diameter(mm) | Notes (orientation, special settings, etc.)
Bottle_Opener_30.stl | 1 | 3:47 | 37 | 50 | No Support | 0.2/0.4 | Adjust number of perimeters to 3-4.
Bottle_Opener_35.stl | 1 | 3:44 | 36 | 50 | No Support | 0.2/0.4 | Adjust number of perimeters to 3-4.
Bottle_Opener_40.stl | 1 | 3:46 | 36 | 50 | No Support | 0.2/0.4 | Adjust number of perimeters to 3-4.
Bottle_Opener_45.stl | 1 | 3:51 | 38 | 50 | No Support | 0.2/0.4 | Adjust number of perimeters to 3-4.
Bottle_Opener_50.stl | 1 | 4:01 | 39 | 50 | No Support | 0.2/0.4 | Adjust number of perimeters to 3-4.

### Post-Processing

- Remove any burrs or sharp edges that may occur if applicable.

### Customization Options

- There are parameters given in the CAD file (.f3d) to change the cap size and handle size if desired.
- Can be printed in any colour.

## 3D PRINTING GUIDE

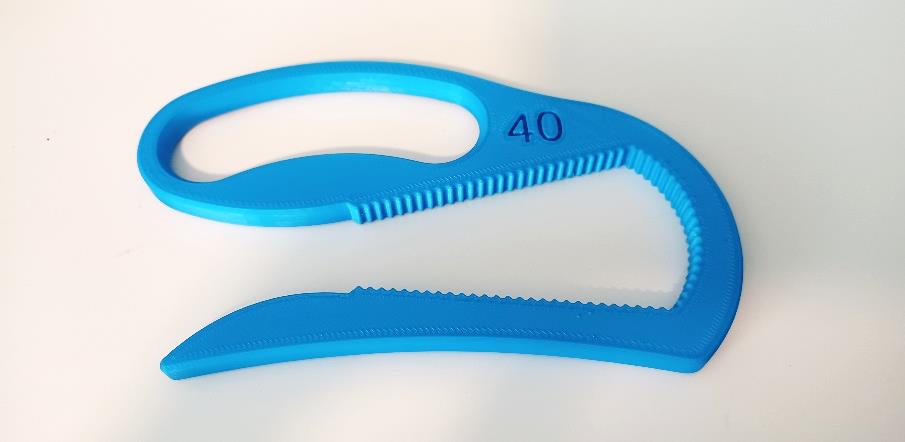
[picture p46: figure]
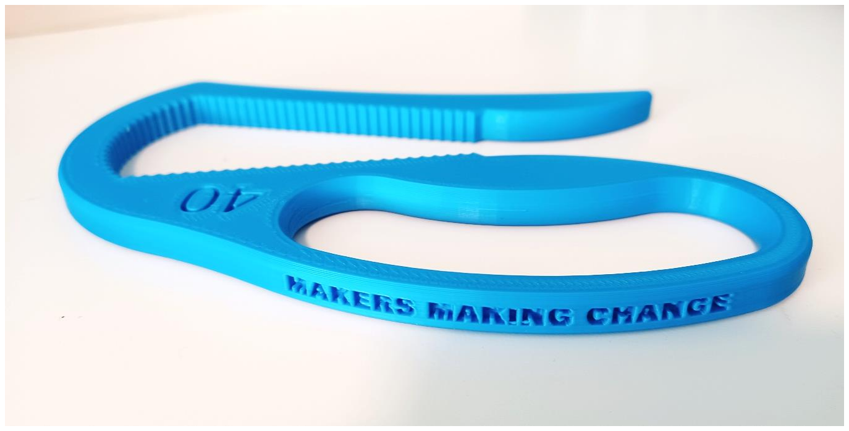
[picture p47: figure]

© 2022 by Neil Squire / Makers Making Change.

### Examples of Quality Prints:

Example of Bottle Opener 40

Example of Bottle Opener 40

## 3D PRINTING GUIDE

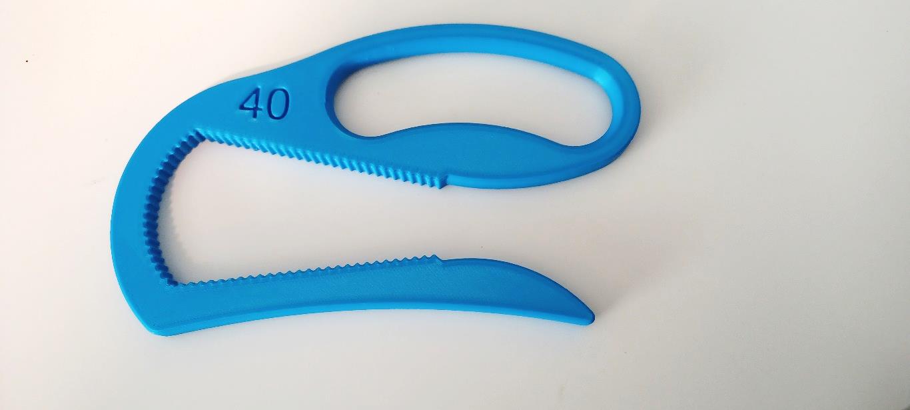
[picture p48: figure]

© 2022 by Neil Squire / Makers Making Change.

Example of Bottle Opener 40

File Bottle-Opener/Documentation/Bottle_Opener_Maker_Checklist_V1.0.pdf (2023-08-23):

V1.0 | May 2022

## Bottle Opener

## MAKER CHECKLIST

© 2022 by Neil Squire / Makers Making Change This work is licensed under the CC BY SA 4.0 License: http://creativecommons.org/licenses/by-sa/4.0 Files available at https://makersmakingchange.com/project/bottle-opener/

## Maker To Do List

Talk to User about which bottles they would like to open, determine which sizes of Bottle Opener to print using the Printable Sizing Chart or examples list.
Ask user about which colour they would prefer the device to be printed in.
Print and test the device/devices.
Print User Guide.

## Items to Give to User

Printed, tested device/devices. User Guide.

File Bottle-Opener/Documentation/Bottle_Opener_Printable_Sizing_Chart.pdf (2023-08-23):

To check if scale is correct,
the line below should be 100mm long.

50mm

45mm

40mm

35mm

30mm

# Printable Sizing Chart for Bottle Opener

To ensure a correct fit,

## bottle caps should fit

within the lines shown.

© 2022 by Neil Squire / Makers Making Change. This work is licensed under the CC BY SA 4.0 License: hp://creavecommons.org/licenses/by-sa/4.0
Files available at hps://makersmakingchange.com/project/bole-opener/ | Page 1 of 1

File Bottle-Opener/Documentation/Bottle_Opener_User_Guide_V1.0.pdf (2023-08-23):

V1.0 | May 2022

## Bottle Opener

## USER QUICK GUIDE

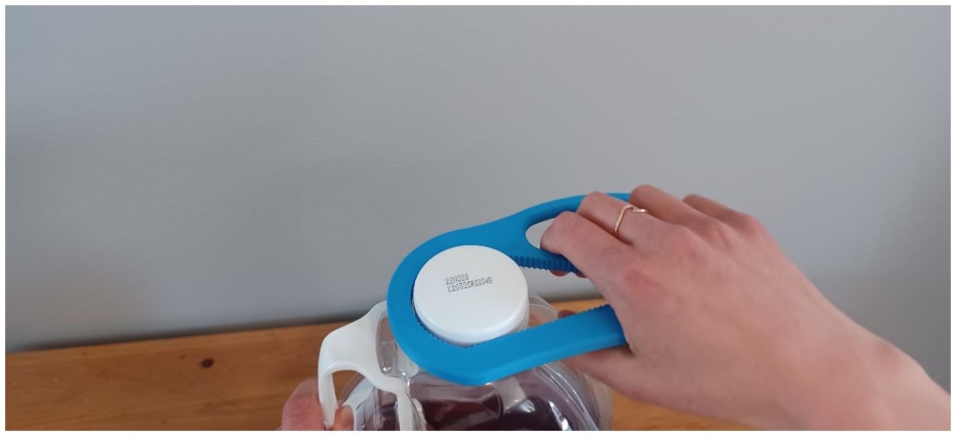
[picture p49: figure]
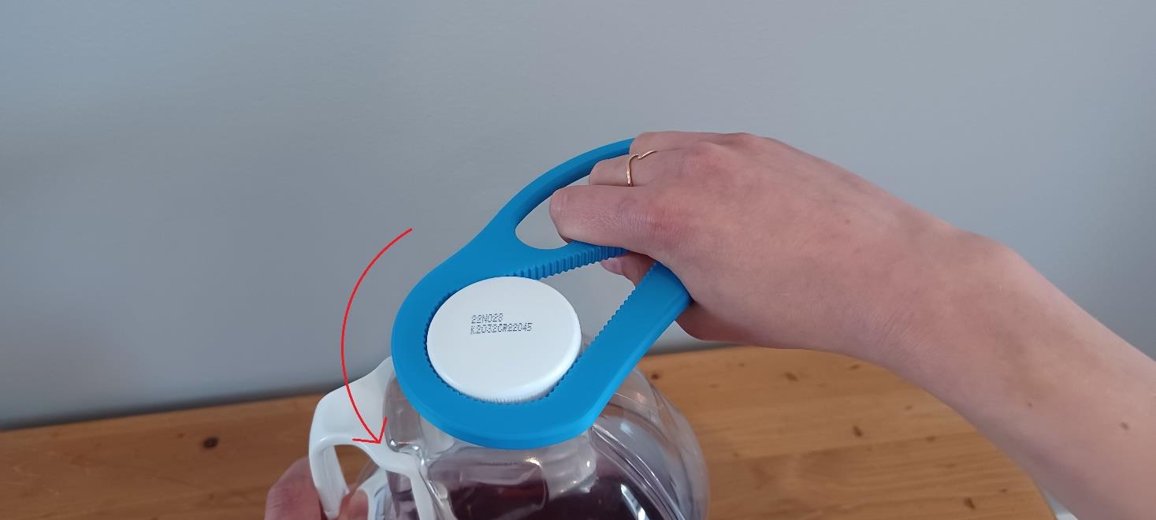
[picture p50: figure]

© 2022 by Neil Squire (https://neilsquire.ca/) / Makers Making Change. This work is licensed under the CC BY SA 4.0 License: http://creativecommons.org/licenses/by-sa/4.0 Files available at https://makersmakingchange.com/project/bottle-opener/

### Introduction

The Large Bottle Opener is a tool to help those with arthritis, limited finger dexterity or other related disabilities open the screw-on caps commonly seen on large juice jugs.

### Usage

Grip the bottle opener with fingers placed though the hole and palm on the bottom lever. Place the bottle opener over the lid of the bottle, squeeze the lever while twisting the cap off the bottle.

## USER QUICK GUIDE

© 2022 by Neil Squire (https://neilsquire.ca/) / Makers Making Change.

### Compatibility

Bottle Opener
Version

Compatible
Diameter of
Caps

Examples of compatible
Bottles and Containers
(May vary between brands)

Image Example of compatible Bottles

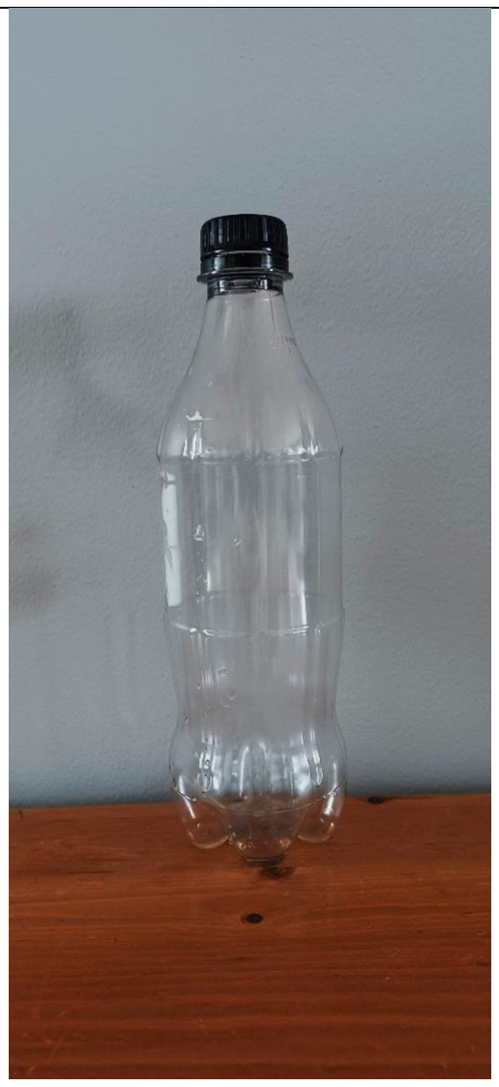
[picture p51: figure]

Bottle Opener
30 | 28 – 30 mm
- Pop bottles of all
sizes (355 mL to 2 L)
- Bottled Water of all
sizes (355 mL to 2 L)
- Milk Carton 2 L
- Juice Carton 2 L

## USER QUICK GUIDE

© 2022 by Neil Squire (https://neilsquire.ca/) / Makers Making Change.

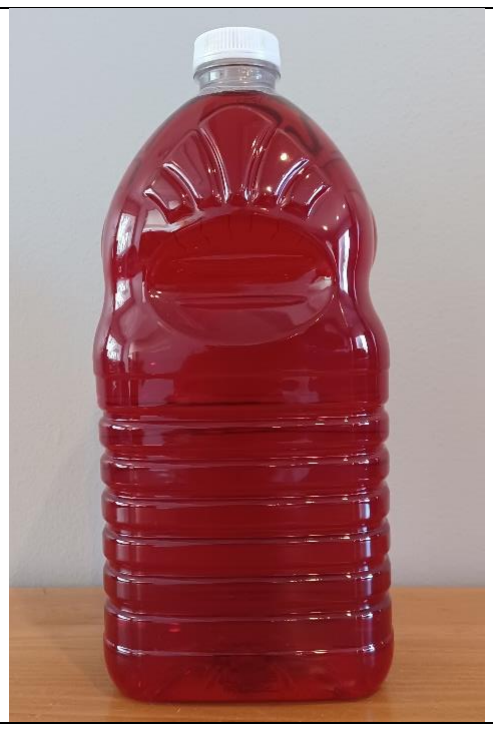
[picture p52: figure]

Bottle Opener 35 | 33 – 36 mm | • Juice Jug (Some brands) 1.89 L • Ketchup Bottle 1 L • Juice Carton 900 mL

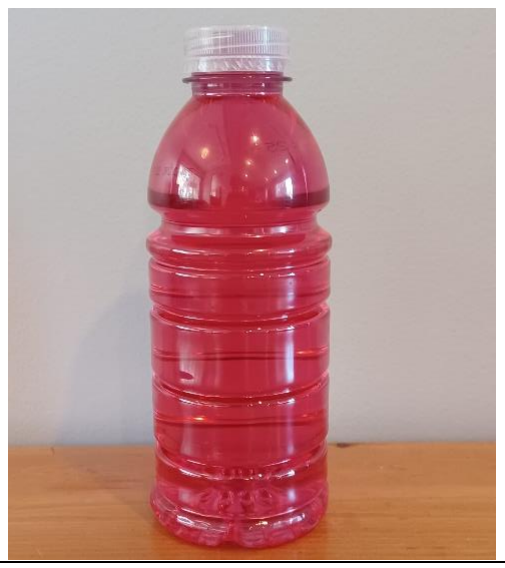
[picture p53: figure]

Bottle Opener 40 | 38 – 41 mm | • Sports Drink 591 mL • Sports Drink 950 mL • Juice Bottle 473 mL • Iced Tea Bottle 473 mL • Milk Bottle 473 mL • Milk Jug 2 L • Milk Jug 4 L • Kefir Bottle 1 L
Bottle Opener 45 | 43 – 46 mm | • Juice Jug 1.46 L • Juice Jug (Some Brands) 1.89 L • Juice Jug 945 mL

## USER QUICK GUIDE

© 2022 by Neil Squire (https://neilsquire.ca/) / Makers Making Change.

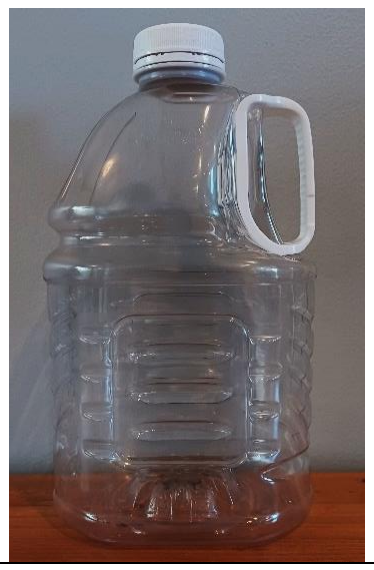
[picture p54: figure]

Bottle Opener
50 | 48 – 51 mm | • | 3 L Juice Jug

### Cleaning


Clean with damp cloth, sterilize with disinfecting wipes or light spray. Do not submerge.

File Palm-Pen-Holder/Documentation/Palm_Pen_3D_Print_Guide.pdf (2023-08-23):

V1.0 | Sept 2021

## Palm Pen

## 3D PRINTING GUIDE


© 2022 by <Author>.


This work is licensed under the CC BY SA 4.0 License: http://creativecommons.org/licenses/by-sa/4.0
Files available at <Replace with MMC Library Link> | Page 1 of 1

### 3D Printing Summary

Palm Pen Size
Metrics | Small | Medium | Large
Total Print Time (min) | 170 | 200 | 240
Total Number of Components | 1 | 1 | 1
Typical Total Mass (g) | 23 | 30 | 35
Typical Number of Print Setups | 1 | 1 | 1

### 3D Printing Settings

Print File Name | Qty | Total Print Time (hr:min) | Mass (g) | Infill (%) | Support (Y/N) | Layer Height/ Nozzle Diameter (mm) | Notes (orientation, special settings, etc)
x_Palm_Pen_y_Pen_hole.S TL where “x” is the palm pen device sizing and “y” is the pen hole sizing | 1 | 170-240 | 23-35 | 20 | N | 0.2/0.4 | - Print in orientation given when brought onto slicer bed

### Post-Processing

- If you notice any blobs on the side of the device try using a blade to clean up the prints.

### Customization Options

- If different sizing is required for the pen hole or palm pen diameter the sizes can be altered using the OpenSCAD file found on the GitHub “design files” folder. Access to the GitHub can be found on the project page of this device.

### Examples of Quality Prints:

- Below are photos of what print quality is expected from printing this device.

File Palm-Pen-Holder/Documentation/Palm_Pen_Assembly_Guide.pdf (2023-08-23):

Required Materials: 1. 1x M4- 0.70 X 16 Machine Screw 2. 1x M4- 0.70 Machine Screw Nut 3. Writing Device (ex: Pen, Paintbrush, Pencil, etc) 4. 1x 3D Printed Palm Pen Holder

© 2023 by <Author>. This work is licensed under the CC BY SA 4.0 License: http://creativecommons.org/licenses/by-sa/4.0
Files available at <Replace with MMC Library Link> | Page 1 of 3
V1.1 | June 2023

## Palm Pen Holder

## ASSEMBLY GUIDE

Required Components

Required Tools

- 3D printer
- Screwdriver

Required Personal Protective Equipment (PPE)

- Safety Glasses


Files available at <Replace with MMC Library Link> | Page 2 of 3
V1.1 | June 2023

## Palm Pen Holder

## ASSEMBLY GUIDE

Assembly Instructions

Step 1
Gather materials needed and ensure that all of the holes in the Palm Pen holder are not obstructed by extra filament. If any holes are, attempt to remove extra filament with a blade or tweezers.
Step 2
Insert the set screw nut into the rectangular slot on the outside face of the Palm Pen Holder. The M4 nut should slide in snugly, you may have to assist it with a screwdriver or writing device.

## Palm Pen Holder

## ASSEMBLY GUIDE


V1.1 | June 2023
Files available at <Replace with MMC Library Link> | Page 3 of 3
Step 3
Now gently thread on the set screw in the hole on the top of the device. This set screw will be used to fix the writing device while in the pen hole.
Step 4
Insert the writing device and tighten the set screw so the chosen writing utensil is fixed.

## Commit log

2026-02-05 Updating all files
    - Making sure all files are up-to-date
    - Reorganizing folders to follow current folder organization
    [Bottle_Opener_30.f3d, Bottle_Opener_30.stl, Bottle_Opener_35.f3d, Bottle_Opener_35.stl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]
2026-02-05 Added Rumble Plate Dice Roller files
    Added all files for the Rumble Plate Dice Roller
    - Had issues when calling the folder "Rumble-Plate-Dice-Roller" (would not commit, or said it was a submodule)
    [Rumble_Plate_BOM.xlsx, Rumble_Plate_Base.stl, Rumble_Plate_Button.stl, Rumble_Plate_Cam.stl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]
2026-02-05 Reorganized files and removed excess files
    - Reorganized folder structure to put 3D print files under Build_Files
    - Removed changelog, version files, and design files
    - Removed spaces from names of files
    [Large_Palm_Pen_Large_Pen_hole.stl, Large_Palm_Pen_Med_Pen_hole.stl, Large_Palm_Pen_Small_Pen_hole.stl, Med_Palm_Pen_Large_Pen_hole.stl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]
2026-02-05 Reorganized files
    - Reorganized files
    - Removed superfluous files
    - Renamed files to better describe contents
    [Large_Pen_ball_Large_Pen_hole.stl, Large_Pen_ball_Medium_Pen_hole.stl, Large_Pen_ball_Small_Pen_hole.stl, Medium_Pen_ball_Large_Pen_hole.stl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]
